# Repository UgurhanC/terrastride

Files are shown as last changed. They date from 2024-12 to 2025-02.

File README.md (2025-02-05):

# TerraStride: An Autonomous Robot for Minimally Invasive Wildlife Monitoring

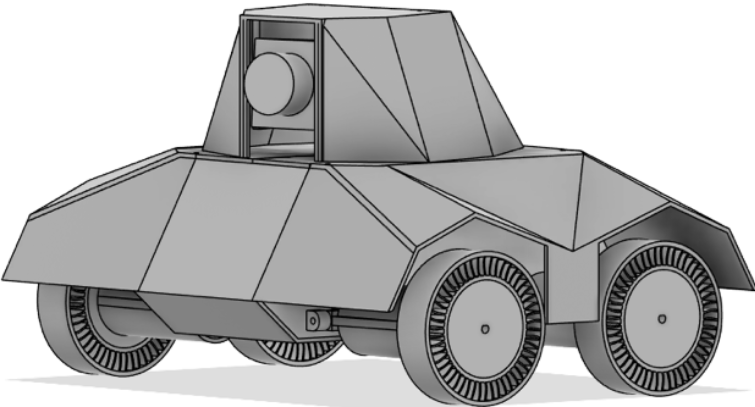
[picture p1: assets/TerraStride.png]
TerraStride Robot


---

## About the Project 🌍

TerraStride is an autonomous robotic vehicle designed to overcome limitations in traditional wildlife monitoring technologies. By leveraging biomimetic design principles and cutting-edge AI, TerraStride enables minimally invasive, dynamic monitoring of wildlife behavior in natural habitats. It integrates advanced computer vision, low-light enhancement, and stealth technologies to reduce disruptions to animals while collecting high-quality data.

### Key Features 🌟

- **🦉 Non-invasive Monitoring**: Tracks and follows animals with minimal disturbance.
- **🤖 Advanced Computer Vision**: Utilizes YOLO and Hailo 8L accelerators for real-time object detection.
- **🌌 Low-Light Performance**: Employs biomimetic image enhancement inspired by nocturnal organisms.
- **🐾 Biomimetic Design**: Features cat-paw-inspired wheels and tortoise-shell camouflage for stealth.
- **📸 Dynamic Data Capture**: Stores high-quality images and videos, optimizing storage through confidence thresholds and motion triggers.

---

## Table of Contents 📑

- [About the Project 🌍](#about-the-project-🌍)
- [Getting Started 🚀](#getting-started-🚀)
- [Usage 🔧](#usage-🔧)
- [Acknowledgments 🙏](#acknowledgments-🙏)

---

## Getting Started 🚀

### Prerequisites 📋

Ensure the following tools and libraries are installed:

- Python 3.9 or later
- Hardware dependencies:
  - Arducam 5MP OV5647DS PTZ Camera 📷
  - Raspberry Pi 5 with Hailo 8L AI accelerator 🤖

### Installation 🛠️

1. **Clone the repository**:

   ```bash
   git clone https://github.com/UgurhanC/terrastride.git
   cd terrastride
   ```

2. **Set up the hardware**:

   - Attach the camera module, motors, and AI accelerator.
   - Follow the assembly instructions in the [hardware guide](3dmodel/build%20instructions.pdf).
   - As for logging into the Raspberry Pi, use the following credentials:
   - Username: terrastride
   - Password: raspberry

3. **Run the system**:

   ```bash
   ./run.sh
   ```

---

## Usage 🔧

To run the full TerraStride system, execute the following command:

```bash
./run.sh
```

This script handles all necessary setup and executes the required modules for the robot’s operation, including locomotion, tracking, and low-light enhancement.

---

## Acknowledgments 🙏

Special thanks to:

- **🎥 Ignas van Schaick** for insights on wildlife filmmaking.
- **📊 Dr. Emiel van Loon** for guidance on ecological tracking.
- **🌲 Dr. Richard Bischof** for expertise on stealth and ecological data collection.
- **💻 Professor Shaodi You** for contributions to real-time video processing.

This project was made possible by collaboration with ecological researchers, computer vision experts, and nature documentary filmmakers.

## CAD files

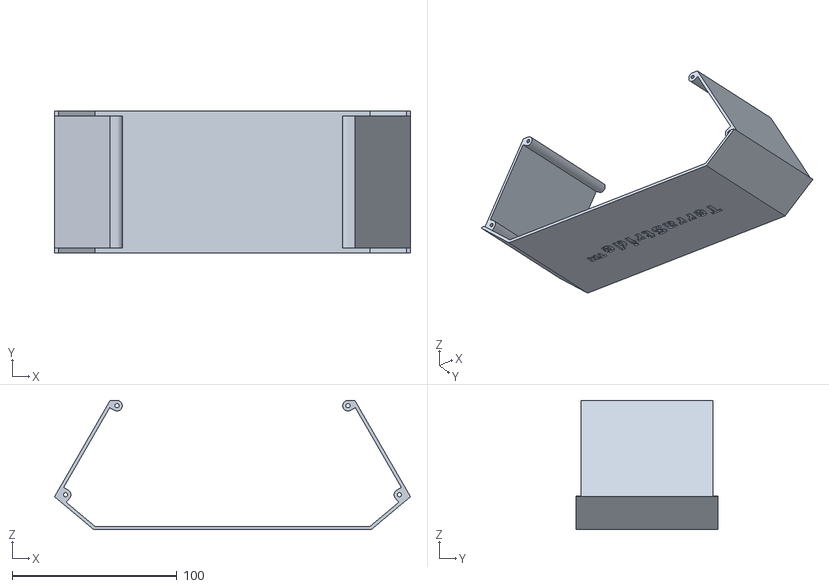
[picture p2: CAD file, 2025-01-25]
3dmodel/Main_Body.stl
216.2 x 86.0 x 78.5

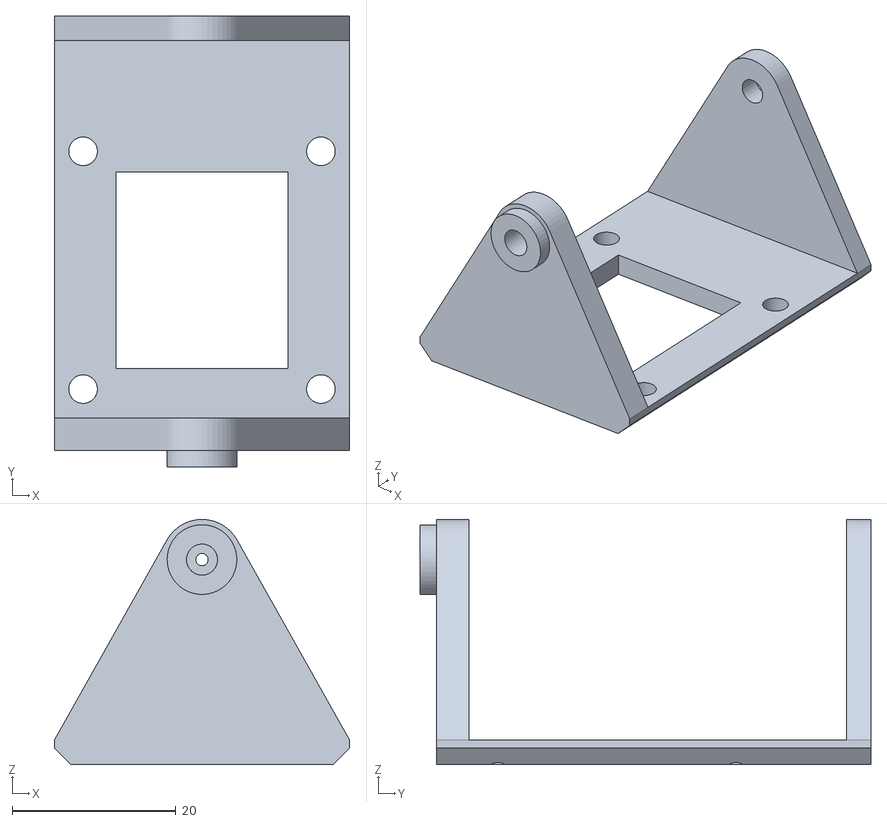
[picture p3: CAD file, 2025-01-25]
3dmodel/swivel.stl
36.0 x 55.0 x 29.9

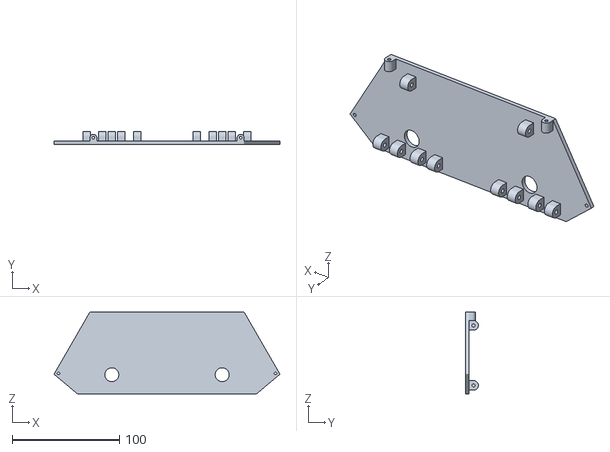
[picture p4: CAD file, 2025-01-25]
3dmodel/Hingeplate.stl
211.0 x 12.0 x 76.5

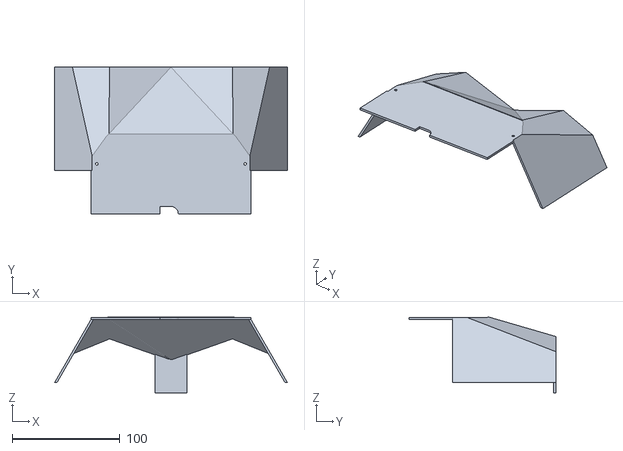
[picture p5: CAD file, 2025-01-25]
3dmodel/Cybershell_right.stl
216.2 x 136.0 x 70.3

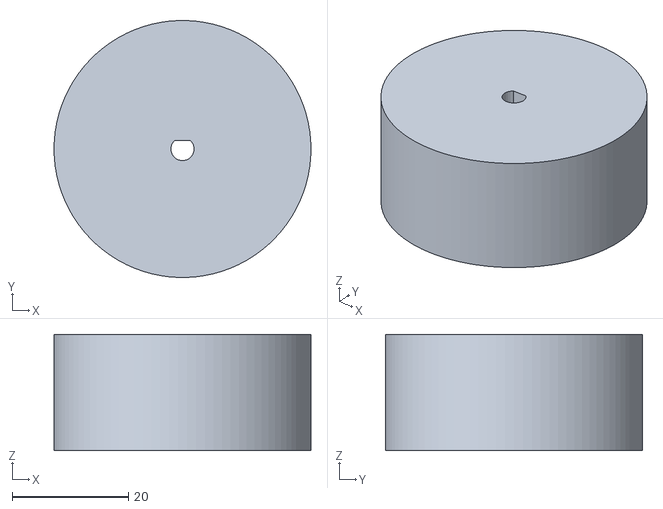
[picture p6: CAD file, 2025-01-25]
3dmodel/Wheel_internal.stl
44.3 x 44.3 x 20.0

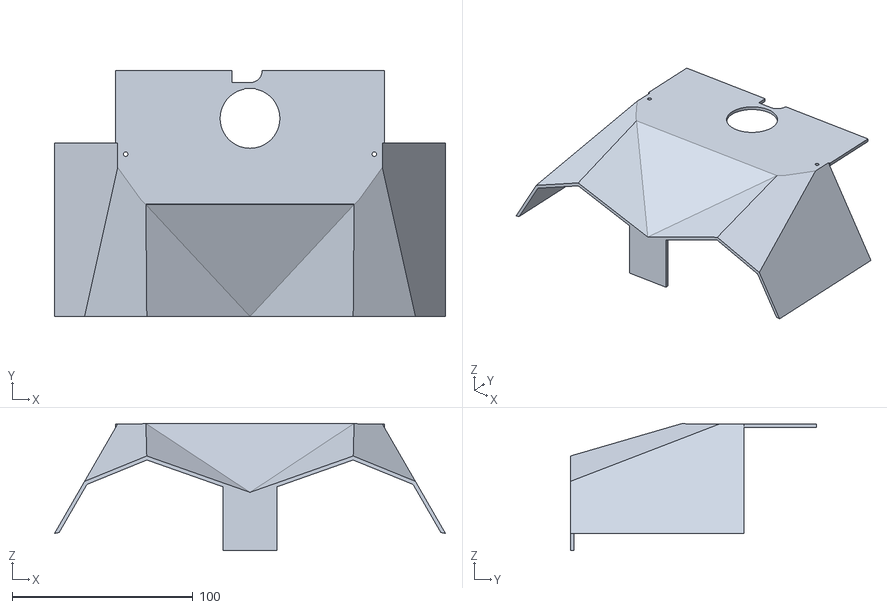
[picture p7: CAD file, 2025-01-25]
3dmodel/Cybershell_left.stl
216.2 x 136.0 x 70.3

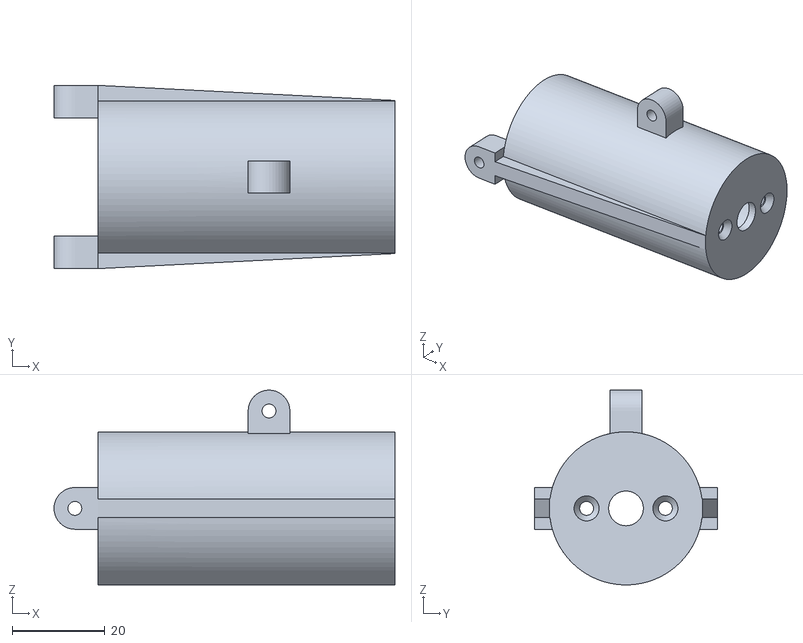
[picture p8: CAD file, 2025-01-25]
3dmodel/Motor_holder.stl
73.5 x 39.5 x 42.0

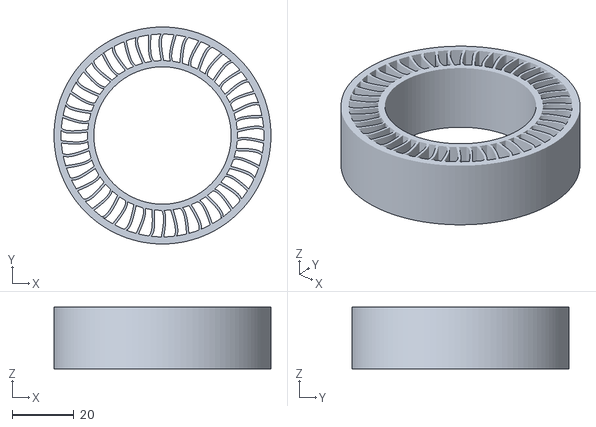
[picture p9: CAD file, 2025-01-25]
3dmodel/Nonpneumatic_wheel.stl
70.0 x 70.0 x 20.0

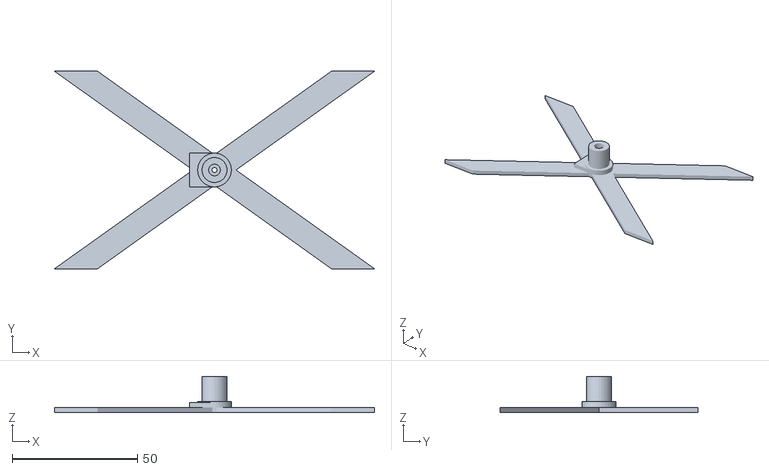
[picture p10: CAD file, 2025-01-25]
3dmodel/Cybershell_pin.stl
128.0 x 79.0 x 14.5

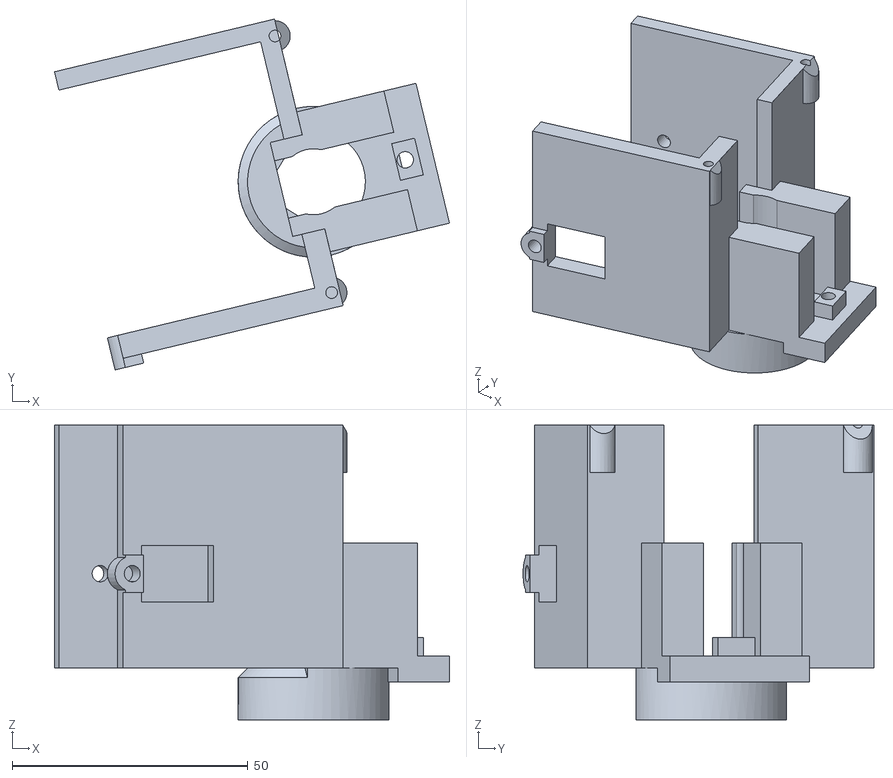
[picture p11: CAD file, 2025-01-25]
3dmodel/Turner.stl
83.8 x 74.4 x 62.5

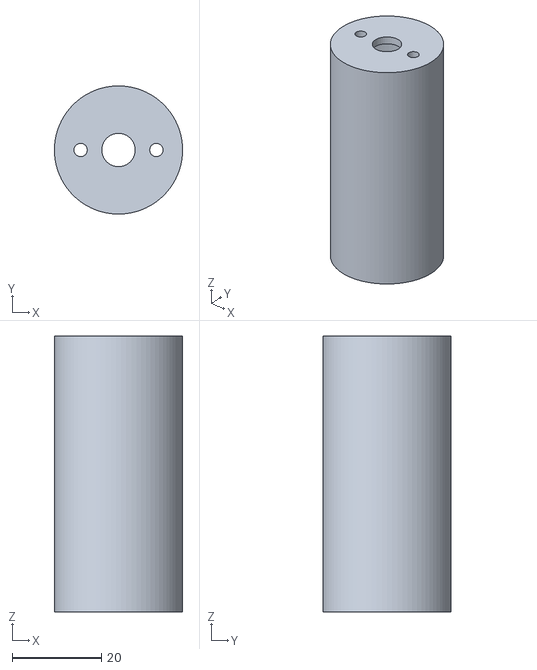
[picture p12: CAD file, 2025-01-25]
3dmodel/Motor_holder_insert.stl
28.8 x 28.8 x 62.0

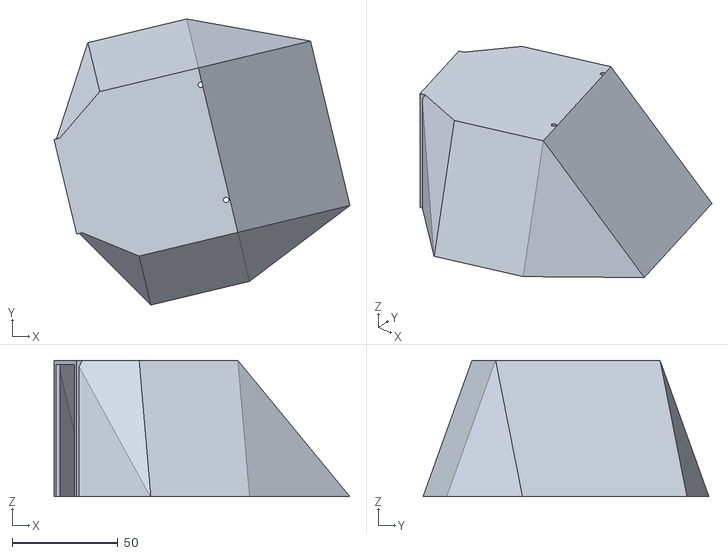
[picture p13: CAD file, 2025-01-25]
3dmodel/enclosure.stl
140.0 x 135.3 x 64.5

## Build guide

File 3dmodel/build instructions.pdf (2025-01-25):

Physical assembly

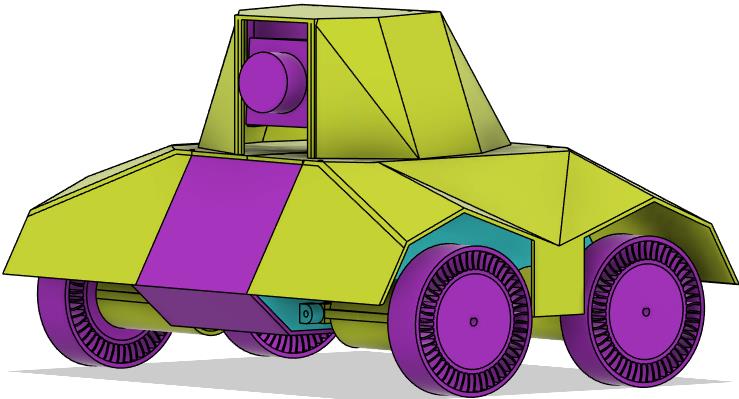
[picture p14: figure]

Print in PLA

- 1x Cybershell left
- 1x Cybershell right
- 1x Cybershell pin
- 2x hingeplate
- 1x main body
- 4x motor holder
- 1x swivel
- 1x enclosure
- 1x turner
- 4x wheel internal

All 80 percent infill except for wheel internal that on 15 percent infill

Print in TPU 95A

- 4x nonpneumatic wheel
- 4x motor holder insert

80 percent infill

Other parts needed

- 1x Raspberry pi + ai kit with all the code on it
- 2x joy-IT SBC-MotoDriver2
- 1x 5000mAh 11.1-volt LiPo
- 1x SG90 Servo
- Reely Micro-servo Digitale servo Materiaal (aandrijving): Kunststof Stekkersysteem: JR
- 1x Reely 1:10 Hydraulische schokdempers Zwart-blauw Met veren Zwart 1 stuk(s)
- 1x Arducam 5MP OV5647DS PTZ Camera for Raspberry Pi 4/3B+/3
- 1x usb a to c cable
- 1x plug for LiPo
- Cables
- Nuts bolts and

Locomotion

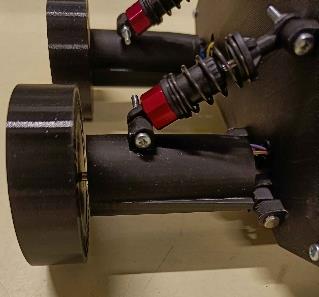
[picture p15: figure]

1. Fit a wheel internal on each motor with a hammer and then take it out. This is to make the connection fit
2. Then solder a wire to each motor
3. Insert the motor holder insert into the motor holder make sure all holes line up.
4. Insert the motor and bolt it down tight. Use these m3 bolts:
5. Guide the wires though the hole of the Hingeplate.
6. Bolt the shock dampers to the motor holder with m3 bolts and m3 locking nuts.
7. Then bolt it all to the hingeplate.
8. Then fit the nonpneumatic wheels over the wheel internal.
9. Place the wheels on the motors.
10. Screw the hingeplates to the main body.

Pan tilt

1. glue the Cybefrshell together with superglue like this:

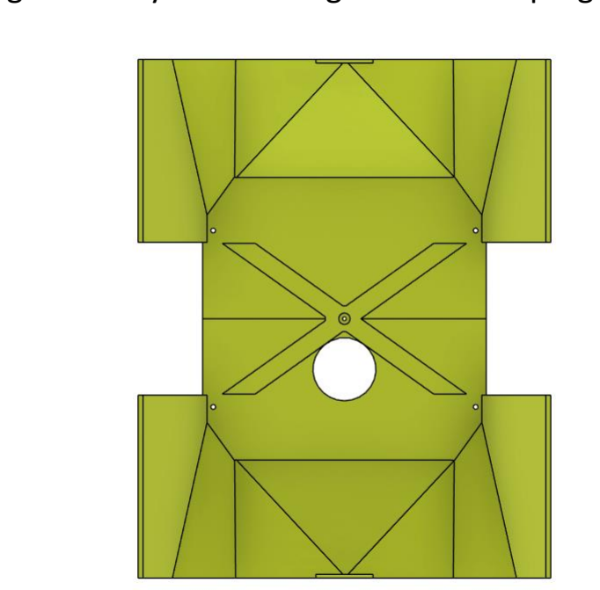
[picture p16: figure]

2. take the turner and insert a bearing might need a vice to put it in
3. take the turner and mount the hingeplate to it with m3 locking nut and m3 bolt

4. place the reely servo and screw it into the hingeplate with the included screw from the sevo.
5. Screw in the sevo to the to the swivel

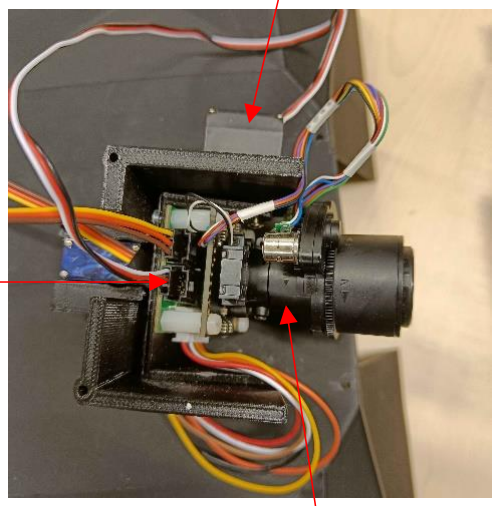
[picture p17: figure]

6. Take the camera parts and make sure they line up like the picture. Use only 4 of the included

bolts to connect the this to the white offsets. Connect the rest with these
bolts again directly to the hingeplate.
7. Take the blue servo and cut off the screw in flap closest to the white turning thing.
8. Screw in the servo.
9. Put the assembly into the pin of the Cybershell make sure the blue servo is inserted into the hole of the pin might need to drill out the hole a bit.
10. Screw blue servo to the Cybershell pin.
11. Screw the enclosure to the Turner
12. Plug the servos into the plugs on the camera module

electronics

1. Solder the LiPo plug in that it splits to the two motor controllers.
2. Add a ground from the LiPo to the raspberry pi.
3. Connect the motors to the motor controllers. Back wheels to the same and front wheels to the same
4. Connect the motor controllers to the raspberry pi. (there will come a update with all connections mapped out.

Final assembly

1. Plug in the motor controllers and the raspberry pi
2. Place the power bank in the main body. Then the LiPo on top.
3. Connect the camera through ribbon cable and pint to the raspberry pi through the hole.
4. Fit everything into the main body.
5. Screw on the Cybershell to the Hingeplates
6. Done.

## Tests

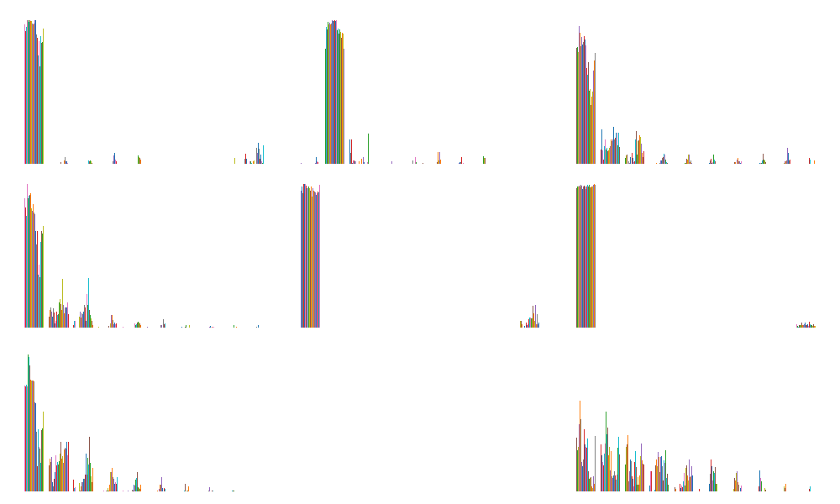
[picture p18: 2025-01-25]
ImageEnhancement/TestingFigures/darkiamge18enhancedHistograms.png

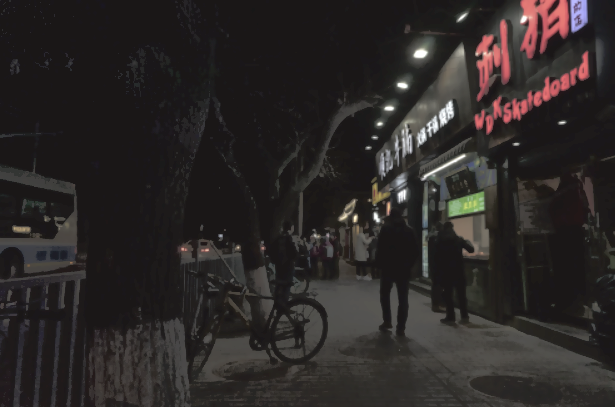
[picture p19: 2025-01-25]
ImageEnhancement/enhanced_image_test.png

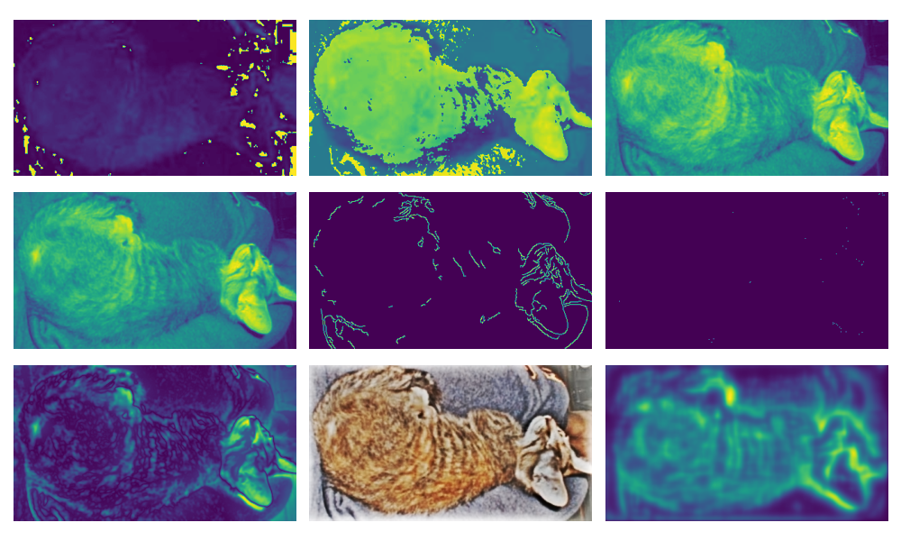
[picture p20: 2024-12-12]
ImageEnhancement/TestingFigures/NaturalCat0001DecompsImages.png

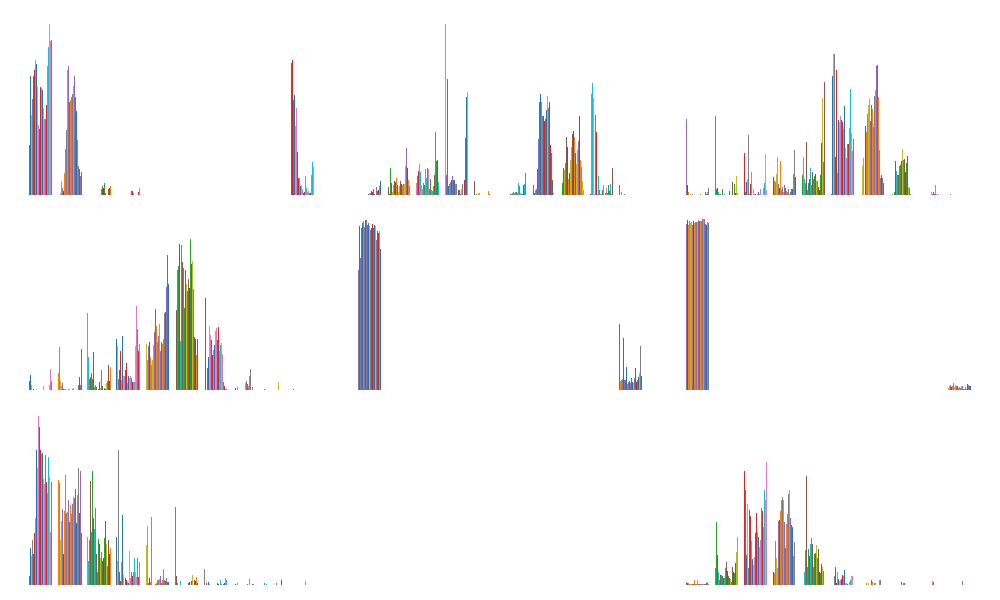
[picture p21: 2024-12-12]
ImageEnhancement/TestingFigures/NaturalCatDecompsHistograms.png

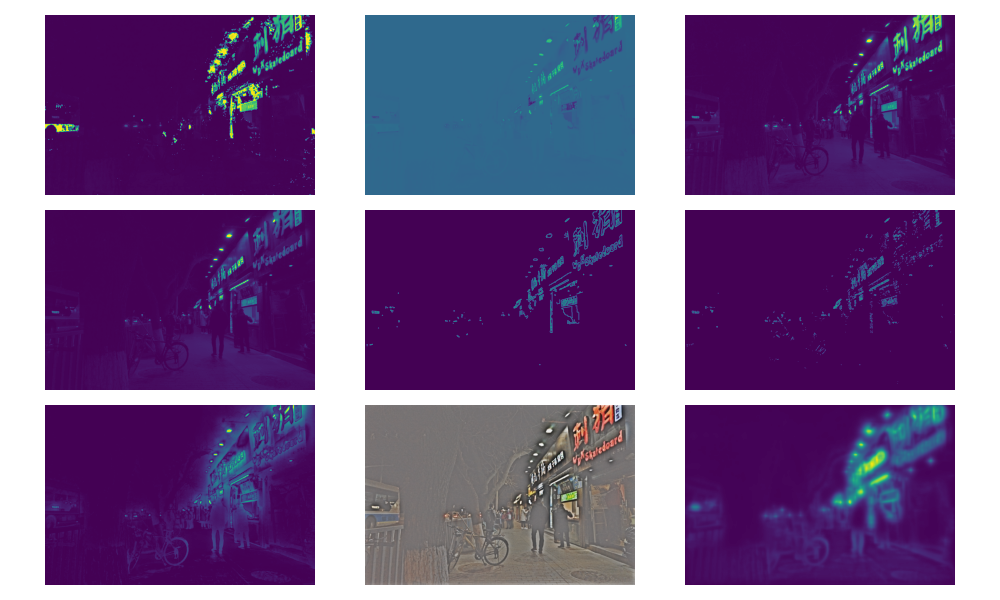
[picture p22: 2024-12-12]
ImageEnhancement/TestingFigures/LowLight18DecompsImages.png

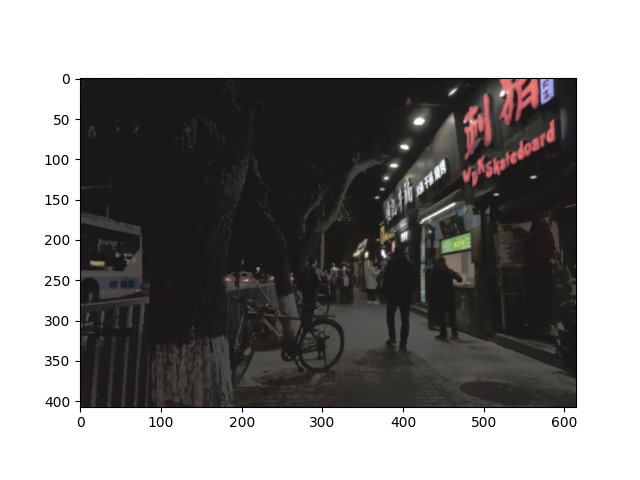
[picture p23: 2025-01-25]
ImageEnhancement/TestingFigures/Enhanced_Image.png

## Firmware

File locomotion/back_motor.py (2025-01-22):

import RPi.GPIO as GPIO
import time

# GPIO Pins (same as your current setup)
LEFT_MOTOR1_IN1 = 22  # Left Motor 1 Forward
LEFT_MOTOR1_IN2 = 23  # Left Motor 1 Backward
LEFT_MOTOR2_IN1 = 9  # Left Motor 2 Forward
LEFT_MOTOR2_IN2 = 25  # Left Motor 2 Backward
LEFT_PWM = 24         # PWM speed control for left motors

RIGHT_MOTOR1_IN3 = 17  # Right Motor 1 Forward
RIGHT_MOTOR1_IN4 = 27 # Right Motor 1 Backward
RIGHT_MOTOR2_IN3 = 11 # Right Motor 2 Forward
RIGHT_MOTOR2_IN4 = 8  # Right Motor 2 Backward
RIGHT_PWM = 10        # PWM speed control for right motors

# Setup GPIO
GPIO.setmode(GPIO.BCM)
GPIO.setup(LEFT_MOTOR1_IN1, GPIO.OUT)
GPIO.setup(LEFT_MOTOR1_IN2, GPIO.OUT)
GPIO.setup(LEFT_MOTOR2_IN1, GPIO.OUT)
GPIO.setup(LEFT_MOTOR2_IN2, GPIO.OUT)
GPIO.setup(LEFT_PWM, GPIO.OUT)

GPIO.setup(RIGHT_MOTOR1_IN3, GPIO.OUT)
GPIO.setup(RIGHT_MOTOR1_IN4, GPIO.OUT)
GPIO.setup(RIGHT_MOTOR2_IN3, GPIO.OUT)
GPIO.setup(RIGHT_MOTOR2_IN4, GPIO.OUT)
GPIO.setup(RIGHT_PWM, GPIO.OUT)

# Initialize PWM
FREQ = 100  # Frequency in Hz
left_pwm = GPIO.PWM(LEFT_PWM, FREQ)  # PWM on LEFT_PWM pin
left_pwm.start(0)  # Start with motors disabled

right_pwm = GPIO.PWM(RIGHT_PWM, FREQ)  # PWM on RIGHT_PWM pin
right_pwm.start(0)  # Start with motors disabled

# Stop all motors
def stop_all_motors():
    print("Stopping all motors...")
    # Stop left motors
    GPIO.output(LEFT_MOTOR1_IN1, GPIO.LOW)
    GPIO.output(LEFT_MOTOR1_IN2, GPIO.LOW)
    GPIO.output(LEFT_MOTOR2_IN1, GPIO.LOW)
    GPIO.output(LEFT_MOTOR2_IN2, GPIO.LOW)
    left_pwm.ChangeDutyCycle(0)
    
    # Stop right motors
    GPIO.output(RIGHT_MOTOR1_IN3, GPIO.LOW)
    GPIO.output(RIGHT_MOTOR1_IN4, GPIO.LOW)
    GPIO.output(RIGHT_MOTOR2_IN3, GPIO.LOW)
    GPIO.output(RIGHT_MOTOR2_IN4, GPIO.LOW)
    right_pwm.ChangeDutyCycle(0)

# Function to test a single motor in forward or backward direction
def test_motor(pin1, pin2, motor_name, pwm_pin, direction):
    print(f"Testing {motor_name} motor {direction}...")
    
    # Stop all motors before starting the new movement
    stop_all_motors()
    
    if direction == 'f':  # Forward
        GPIO.output(pin1, GPIO.HIGH)
        GPIO.output(pin2, GPIO.LOW)
    elif direction == 'b':  # Backward
        GPIO.output(pin1, GPIO.LOW)
        GPIO.output(pin2, GPIO.HIGH)
    
    pwm_pin.ChangeDutyCycle(50)  # Adjust speed to 50% for visibility
    time.sleep(2)  # Motor should run for 2 seconds
    
    # Stop motor
    stop_all_motors()
    print(f"Stopped {motor_name} motor.")

# Main loop for testing motors via user input
def motor_test():
    while True:
        # Get input command
        user_input = input("Enter motor command (e.g. r1f for Right Motor 1 Forward, l2b for Left Motor 2 Backward, or 'exit' to quit): ").lower()
        
        if user_input == 'exit':
            print("Exiting motor test...")
            break
        
        # Validate and map the user input to the correct motor and direction
        if len(user_input) == 3:
            motor = user_input[0]  # 'r' or 'l' for Right or Left
            motor_num = int(user_input[1])  # 1 or 2 for motor 1 or 2
            direction = user_input[2]  # 'f' for Forward, 'b' for Backward

            if motor == 'r' and motor_num == 1:
                # Right Motor 1
                test_motor(RIGHT_MOTOR1_IN3, RIGHT_MOTOR1_IN4, "Right Motor 1", right_pwm, direction)
            elif motor == 'r' and motor_num == 2:
                # Right Motor 2
                test_motor(RIGHT_MOTOR2_IN3, RIGHT_MOTOR2_IN4, "Right Motor 2", right_pwm, direction)
            elif motor == 'l' and motor_num == 1:
                # Left Motor 1
                test_motor(LEFT_MOTOR1_IN1, LEFT_MOTOR1_IN2, "Left Motor 1", left_pwm, direction)
            elif motor == 'l' and motor_num == 2:
                # Left Motor 2
                test_motor(LEFT_MOTOR2_IN1, LEFT_MOTOR2_IN2, "Left Motor 2", left_pwm, direction)
            else:
                print("Invalid command! Please enter a valid motor and direction (e.g., r1f, l2b).")
        else:
            print("Invalid command format! Please use the format: r1f, l2b, etc.")

# Start the motor test
motor_test()

# Clean-up GPIO after tests
GPIO.cleanup()

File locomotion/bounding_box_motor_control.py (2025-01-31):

import RPi.GPIO as GPIO
import time
import locomotion.movement_mapping

# Robot parameters
WHEEL_RADIUS = 0.035  # 3.5 cm
WHEELBASE_WIDTH = 0.15  # 15 cm distance between left and right wheels

# GPIO Pins
# Left side motors
# Occupied pins by cam: 2, 4, 6, 14, 3, 5
# GPIO Pins (same as your current setup)
LEFT_MOTOR1_IN1 = 1 #22  # Left Motor 1 Forward
LEFT_MOTOR1_IN2 = 23  # Left Motor 1 Backward
LEFT_MOTOR2_IN1 = 9  # Left Motor 2 Forward
LEFT_MOTOR2_IN2 = 25  # Left Motor 2 Backward
LEFT_PWM = 18         # PWM speed control for left motors

RIGHT_MOTOR1_IN3 = 27  # Right Motor 1 Forward
RIGHT_MOTOR1_IN4 = 17 # Right Motor 1 Backward
RIGHT_MOTOR2_IN3 = 7 # Right Motor 2 Forward
RIGHT_MOTOR2_IN4 = 11  # Right Motor 2 Backward
RIGHT_PWM = 10        # PWM speed control for right motors


# GPIO Setup
GPIO.setmode(GPIO.BCM)
GPIO.setup(LEFT_MOTOR1_IN1, GPIO.OUT)
GPIO.setup(LEFT_MOTOR1_IN2, GPIO.OUT)
GPIO.setup(LEFT_MOTOR2_IN1, GPIO.OUT)
GPIO.setup(LEFT_MOTOR2_IN2, GPIO.OUT)
GPIO.setup(LEFT_PWM, GPIO.OUT)
GPIO.setup(RIGHT_MOTOR1_IN3, GPIO.OUT)
GPIO.setup(RIGHT_MOTOR1_IN4, GPIO.OUT)
GPIO.setup(RIGHT_MOTOR2_IN3, GPIO.OUT)
GPIO.setup(RIGHT_MOTOR2_IN4, GPIO.OUT)
GPIO.setup(RIGHT_PWM, GPIO.OUT)

# Initialize PWM
left_pwm = GPIO.PWM(LEFT_PWM, 100)  # Frequency at 100 Hz
right_pwm = GPIO.PWM(RIGHT_PWM, 100)
left_pwm.start(0)
right_pwm.start(0)

def move_robot(left_speed, right_speed):
    """
    Control the robot motors using GPIO pins based on left and right speed percentages.
    """
    print("robot moving")
    left_duty_cycle = max(min(left_speed, 100), -100) / 100.0
    right_duty_cycle = max(min(right_speed, 100), -100) / 100.0

    # Left motors direction control
    if left_duty_cycle > 0:
        # Forward direction for left motors
        GPIO.output(LEFT_MOTOR1_IN1, GPIO.HIGH)
        GPIO.output(LEFT_MOTOR1_IN2, GPIO.LOW)
        GPIO.output(LEFT_MOTOR2_IN1, GPIO.HIGH)
        GPIO.output(LEFT_MOTOR2_IN2, GPIO.LOW)
    else:
        # Backward direction for left motors
        GPIO.output(LEFT_MOTOR1_IN1, GPIO.LOW)
        GPIO.output(LEFT_MOTOR1_IN2, GPIO.HIGH)
        GPIO.output(LEFT_MOTOR2_IN1, GPIO.LOW)
        GPIO.output(LEFT_MOTOR2_IN2, GPIO.HIGH)

    # Right motors direction control
    if right_duty_cycle > 0:
        # Forward direction for right motors
        GPIO.output(RIGHT_MOTOR1_IN3, GPIO.HIGH)
        GPIO.output(RIGHT_MOTOR1_IN4, GPIO.LOW)
        GPIO.output(RIGHT_MOTOR2_IN3, GPIO.HIGH)
        GPIO.output(RIGHT_MOTOR2_IN4, GPIO.LOW)
    else:
        # Backward direction for right motors
        GPIO.output(RIGHT_MOTOR1_IN3, GPIO.LOW)
        GPIO.output(RIGHT_MOTOR1_IN4, GPIO.HIGH)
        GPIO.output(RIGHT_MOTOR2_IN3, GPIO.LOW)
        GPIO.output(RIGHT_MOTOR2_IN4, GPIO.HIGH)

    # Adjust PWM for speed
    left_pwm.ChangeDutyCycle(abs(left_duty_cycle * 100))
    right_pwm.ChangeDutyCycle(abs(right_duty_cycle * 100))

    #locomotion.movement_mapping.move_robot(left_speed, right_speed, 0.1)


def stop_robot():
    """
    Stop the robot by setting all GPIO outputs to low.
    """
    #print("robot stopping")
    GPIO.output(LEFT_MOTOR1_IN1, GPIO.LOW)
    GPIO.output(LEFT_MOTOR1_IN2, GPIO.LOW)
    GPIO.output(LEFT_MOTOR2_IN1, GPIO.LOW)
    GPIO.output(LEFT_MOTOR2_IN2, GPIO.LOW)
    GPIO.output(RIGHT_MOTOR1_IN3, GPIO.LOW)
    GPIO.output(RIGHT_MOTOR1_IN4, GPIO.LOW)
    GPIO.output(RIGHT_MOTOR2_IN3, GPIO.LOW)
    GPIO.output(RIGHT_MOTOR2_IN4, GPIO.LOW)
    left_pwm.ChangeDutyCycle(0)
    right_pwm.ChangeDutyCycle(0)

if __name__ == "__main__":
    try:
        print("Robot ready to receive movement commands.")
        # while True:
        #     time.sleep(1)
    except KeyboardInterrupt:
        print("Stopping robot...")
        stop_robot()
    finally:
        GPIO.cleanup()

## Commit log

2024-12-12 Merging everything into this main branch
    [cat_averaged_decomposition_statistics.csv, lowlight_averaged_decomposition_statistics.csv]
2025-01-14 Added folder for locomotion software with code for bounding box based locomotion and motor control.
2025-01-27 Updated random_exploration() and added servo test software.
2025-01-28 Fixed print statement
